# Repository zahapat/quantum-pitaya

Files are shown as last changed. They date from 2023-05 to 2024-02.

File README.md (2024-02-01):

# SQDLab FPGA Environment for Quantum Computing

Welcome to the FPGA Environment for Quantum Computing template repository.

This repository is primarily designed for use with the [Xilinx Vivado Design Suite (HLx Edition build 2020.2)](https://www.xilinx.com/support/download/index.html/content/xilinx/en/downloadNav/vivado-design-tools/archive.html) on Windows platforms.

This repository contains VLSI hardware components, PCB layouts for Red Pitaya boards, and Vivado board files for high-speed data acquisition, clock synthesis, and other purposes within a quantum laboratory.

## Prerequisites

1. [Vivado Design Suite (HLx Edition build 2020.2)](https://www.xilinx.com/support/download/index.html/content/xilinx/en/downloadNav/vivado-design-tools/archive.html)
2. [ModelSim-Intel® FPGA Standard Edition, Version 20.1std](https://www.intel.com/content/www/us/en/software-kit/750637/modelsim-intel-fpgas-standard-edition-software-version-20-1.html?)
3. [Cygwin](https://www.cygwin.com/install.html) (GNU and Open Source tools for Linux-like functionality on Windows)
4. [App Installer (Winget)](https://apps.microsoft.com/store/detail/app-installer/9NBLGGH4NNS1) available on Microsoft Store.
5. Run all scripts in the directory `'./scripts/installers/win11/'` as an administrator to configure environment variables, install chocolate, Microsoft PowerShell, PuTTY, GitHub CLI (gh), and Make.
6. If you wish to install Python as well, uncomment the fourth line in the `'RunAsAdmin2-InstallEssentialAppsWin11.bat'` file using your text editor or run the following command in your favorite terminal:

    ```shell
    choco install -yes python
    ```
7. After installing all the required software, go to the directory of this environment. Open this directory in your favourite terminal and run:
    ```shell
    make sim_init
    ```
    This will create a modelsim.ini file in the environment's root directory, necessary to launch simulations.

## Description

The tools provided with this repository serve to offer tools and VLSI source files for facilitating the development of FPGA-based projects to build optimal and resource-efficient hardware.

One can find the following subdirectories:

1. Tcl

    `./tcl` contains Tcl scripts that interact with software supporting a Tcl (Tickle) console. They are designed for automating project building and running simulations using CLI (command-line interface).

2. Scripts

    The `'./scripts'` directory consists of the following tools:

   - Python-Notebook-Based FQEnv wrapper and control tool
   - The search for optimal MMCM (Mixed Mode Clock Manager) primitives analyzer for optimal clock synthesis
   - FIR Coefficients Generator
   - Generic parameters generator
   - Data Visualizer after successful readout

3. Modules

    The `./modules` directory serves as a repository of HDL modules created throughout the development. These modules consist of hardware description and Tcl scripts for adding files to Vivado Design Suite and Modelsim in correct compile order.

4. Boards

    This directory serves as a repository of Tcl-based generators of Vivado board `'*.bd'` files necessary to integrate the project cores with various AXI-based components. It is possible to inspect such bd file in Vivado IDE.

5. PCB

    The `'./pcb'` directory contains PCB design source files and gerber files to view, review, modify, or adapt PCB designs to new designs using KiCad. Gerber files can be directly sent to a PCB manufacturer.

6. Do

    The `'./do'` directory contains do scripts that enable launching and compiling source files within ModelSim.

7. Simulator

    The `'./simulator'` directory accompanies scripts in the `./do` directory. This is the output directory of the ModelSim simualtor. Also, it contains other basic do scripts to control simulation via the ModelSim Tcl command-line. Do scripts can be programmed using Tcl.

8. Vivado

    This folder contains the Vivado project. While building the project, report files are being generated to inspect the properties of the hardware being generated, its resource utilization, timing, and more. These properties can also be inspected after launching the `FQEnv.xpr` Vivado project file located in this directory.

## Getting Started

The core unit of the FPGA Environment is the central Makefile located in the root direcotry of this repository. When opened in a text editor, it consists variables in upprecase and make targets which are named based on what one intends to do. For example, the `'make src'` target will add sources to Vivado; and `'make board'` will create and add the bd file to vivado. 

The following example reflects the main implementation flow. Run the following commands in your terminal after navigating to the root directory.

- Reset the environment:
    ```shell
    make reset
    ```

- Add all HDL sources under the given the relative Top file located in modules directory. In this case, the TOP variable defined in the Makefile will be explicitly updated by the desired source:
    ```shell
    make src TOP=top_redpitaya_125_14.sv
    ```

- Generate the Systemcerilog header file with FIR filter coefficients. All command-line arguments (e.g. INT_NUMBER_OF_TAPS, INT_COEF_WIDTH, ...) are be specified the following way:
    ```shell
    make gen_fir_coeff INT_NUMBER_OF_TAPS=13 INT_COEF_WIDTH=15 FLOAT_SAMPLING_FREQUENCY_MHZ=125.0 FLOAT_CUTOFF_FREQUENCY_MHZ=25.0
    ```

- Generate a Systemverilog header file with generic variables for the target Top file located in modules directory. The Top file is specified by updating the 'TOP' variable located in the Makefile, as shown below.
    ```shell
    make generics TOP=top_redpitaya_125_14.sv
    ```

- Run a Tcl script to generate and add the target board file, which includes the schematic system design. The target board file is specified by updating the `'BOARD'` variable declared in the Makefile, as shown below:
    ```shell
    make board BOARD=sqdlab_redpitaya_125_14_extclk
    ```

- Run all stages of implementation: synthesis, implementation, bitstream generation, hw platform generatoin (if applicable)
    ```shell
    make all
    ```

- After successful bitstream generation, the following command will copy the output bitfile together with all report available files to the `./output` directory. The output folder will be created if it does not exist.
    ```shell
    make distribute_outputs
    ```

All the abovementioned steps can be executed at once by running the following make target. This will force re-generate the desired build. You can also specify other parameters, such as GEN1_NAME declared in Makefile:
```shell
make build TOP=top_redpitaya_125_14.sv BOARD=sqdlab_redpitaya_125_14_extclk INT_NUMBER_OF_TAPS=13 INT_COEF_WIDTH=15 FLOAT_SAMPLING_FREQUENCY_MHZ=125.0 FLOAT_CUTOFF_FREQUENCY_MHZ=25.0
```

## Programming the RedPitaya board

A specific daughter Makefile is available with make commands dedicated to control the desired RedPitaya board.

To program the 10-bit RedPitaya board, run the following make command:
```shell
make rp_prog1
```

To program the 14-bit RedPitaya board:
```shell
make rp_prog2
```

To program both:
```shell
make rp_prog12
```

To run linux terminal on the 10-bit RedPitaya board:
```shell
make rp_terminal BOARD_LOCALHOST_URL=rp-f07244.local
```

To run linux terminal on the 14-bit RedPitaya board with external clock capability:
```shell
make rp_terminal BOARD_LOCALHOST_URL=rp-f0afdf.local
```

## Accessing the custom hardware of the RedPitaya board

Reading from and writing to the custom-made hardware modules is performed via AXI-Lite interface. Both `'top_redpitaya_125_10.sv'` and `'top_redpitaya_125_14.sv'` are available at the address offset 0x40600000 of the AXI-Lite address space. The `'axi4lite_fifo_readout.vhd'` as part of both of the abovementioned top modules allows for accessing two read channels and two write channels:

1. Read channel 1: address: `0x40600000` (FPGA->PC CDCC buffer FIFO channel 1)
2. Read channel 2: address: `0x40600004` (FPGA->PC CDCC buffer FIFO channel 2)
3. Write Channel 1 address: `0x40600008` (PC->FPGA CDCC buffer FIFO channel 1)
4. Write channel 2 address: `0x40600009` (PC->FPGA CDCC buffer FIFO channel 2)

Communication between the remote PC and the Red Pitaya board is performed via plink CLI commands (Putty). Read (`rp_read`) and write (`rp_write`) make targets are defined in the `'redpitaya.mk'` file.

To read 1024 values from the CDCC buffer FIFO channel 1, and save the output read_ch1.txt to the outputs directory:
```shell
make rp_read ADDRESS=0x40600000 VALUES_CNT=1024 COUT_OUTPUT_DIR=./outputs/ COUT_FILENAME=read_ch1.txt
```

To read 1024 values from the CDCC buffer FIFO channel 2, and save the output `'read_ch2.txt'` to the outputs directory:
```shell
make rp_read ADDRESS=0x40600004 VALUES_CNT=1024 COUT_OUTPUT_DIR=./outputs/ COUT_FILENAME=read_ch2.txt
```

Writing to the specific modules of the FPGA fabric uses a simple protocol. The write channel 1 uses several bits for command specification, module destination identifier, and one bit serves for concatenating the entire 32-bit wide write channel 2 packet to the write channel 1 packet.

The write channel 1 packet contains the following sections:
- *command* bits: 

    [INT_CMD_OUTPUT_WIDTH+INT_MODULE_SELECT_WIDTH : INT_MODULE_SELECT_WIDTH+1]
- module *destination* bits

    [INT_MODULE_SELECT_WIDTH : 1]
- wait for channel 2 data: 

    [0] must be true (0x1) or false (0x0)

The 32-bit wide channel 2 serves as a data channel. Data will be delivered to the destination specified by the write channel 1. The LSB must be set high to concatenate the channel write 1 with the data in the channel write 2, if needed.

If you do not wish to wait for the channel 2 and only want to send one control command throughout the write channel 1, it is possible to specify the command, module destination, and leave the LSB low. However, the required module must support this. Currently, all modules use the write channel 1 and 2 combination approach.

This example illustrates how to update the time integration value to 5. First, specify the module to be controlled:

- *cmd* = 0x0 (no need to set any of these bits high as data will be  TODO)
- *destination* = 0x3 (module  destination of the averager)
- *wait* = 0x1 (wait for channel 2 data is true)

After concatenating *cmd*, *destination*, and *wait* sections of the packet: [0x0, 0x3, 0x1] = 32'b000...0111 = 0x00000007
```shell
make rp_write ADDRESS=0x40600008 RP_CMD=0x00000007
```

Second, the following command will use the write channel 2 to update the new time integration accumulator value:
```shell
make rp_write ADDRESS=0x40600009 RP_CMD=0x00000005
```

It is possible to use up all 32 bits for it, however, the specified module may extract only a lesser number of bits depending on its input and output width specifications. More specifically, the maximum width of the `averager.sv` module to update the averaging(time integration) value is `ceil log2(INT_AVG_MAX_AVERAGE_BY)`. The `INT_AVG_MAX_AVERAGE_BY` can be updated in the main Makefile, and hardware must be re-created by running `make build` command after having this parameter updated, in case this hardware has not been created yet.

The module address map is the following. Note that module destination = 0 is invalid.
1. module destination = 1: `fifo_multichrdctrl.sv` control (both in-phase and quadrature). Select the channel and the number of reads from the `fifo_accumulator.sv` to the CDCC fifo buffer. 

Example: 
`cmd = 0 (select channel 0)` & `module destination = 1 (averager)` & `wait for channel 2 data = 1 (True)` = 0x00000003
```shell
make rp_write ADDRESS=0x40600008 RP_CMD=0x00000003
```

Use the write channel 2 to set the number of reads from the channel 0 FIFO channel. Let's read all items from the single `fifo_accumulator.sv` channel specified by INT_MULTIACC_FIFO_DEPTH in the Makefile = 1024 (0x00000400):
```shell
make rp_write ADDRESS=0x40600009 RP_CMD=0x00000400
```

2. module destination = 2: `fir_parallel.sv` control (in-phase and quadrature). Update the FIR coefficients by selecting the tap ID and its new value.

Example: 
`cmd = 0 (select tap 0)` & `module destination = 2 (FIR)` & `wait for channel 2 data = 1 (True)` = 0x00000005
```shell
make rp_write ADDRESS=0x40600008 RP_CMD=0x00000005
```

Use the write channel 2 to set the FIR coefficient 0 to a new value, e.g. 0xdeadbeef:
```shell
make rp_write ADDRESS=0x40600009 RP_CMD=0xdeadbeef
```

3. module destination = 3: `averager.sv` control (in-phase and quadrature). An example to control this module has been provided in this section above.

4. TODO: module destination = 4: `fifo_multichannel.sv`to vary the number of accumulation repetitions and multichannel FIFO dimensions instead of having it fixed by INT_MULTIACC_REPETITIONS, INT_MULTIACC_FIFO_DEPTH, and INT_MULTIACC_CHANNELS parameters.

## Usuing the FQEnv Python Notebook Makefile Build and Control Tool

*This area is currently under development and new updates are coming soon.*

This repository also contains the `fqenv.ipynb` file that serves as Python-based control tool instead of using a CLI. Also, such tool can be used as a starting point to integrating this FPGA environment into a higher-level Python ecosystem.

Methods declared in the within the `fqenv.py` allow one to perform each step of the process to build the hardware with defined parameters, program the Red Pitaya FPGA board, and control it remotely via Ethernet.

## Git: Create a New Repository

Update the `GIT_EMAIL` variable in `git.mk`. Use your email address to link Git with your Git account.
Run the following command to create a new private repo:

```shell
$ make git_new_private_repo
```

Run the following command to create a new public repository:

```shell
$ make git_new_public_repo
```

Run the following command to make the repository as a template:

```shell
$ make git_make_this_repo_template
```

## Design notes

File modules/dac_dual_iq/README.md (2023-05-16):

## Description

This module performs writing data signals to an DAC connected to the FPGA.

This core is designed for single-ended data signals.

This module has been originaly developed to interface an DAC on the Red Pitaya STEMLab 125-10 board. Therefore, further testing (for example, signal pass-through) should be performed on other devices before using this core on other platforms.

### Main Operation

1. Set generic parameters:
- INT_DAC_CHANNELS: 1 or 2
- INT_DAC_DATA_WIDTH: Enter the number of DAC data bits
- INT_AXIS_DATA_WIDTH: 32 bits typically

2. To synthesize this module in out-of-context mode, do the following:
- make reset
- make src TOP=axis_dac_ad976xastz.v
- make ooc TOP=axis_dac_ad976xastz.v

## TODO
- Add support for differential outputs

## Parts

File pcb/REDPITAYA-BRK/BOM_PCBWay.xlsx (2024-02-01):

 |  |  | xxxx xxxx xxxxx xxPCS BOM (Sample Bill of Materials)
Item # | *Designator | *Qty | Manufacturer | *Mfg Part # | Description / Value | *Package/Footprint | Type | Your Instructions / Notes
1 | ANALOG_OUT_1 | 1 | Hirose Electric Co Ltd | U.FL-R-SMT-1(10) | U.FL (UMCC) Connector Receptacle, Male Pin 50Ohm Surface Mount Solder | HRS_U.FL-R-SMT-1(10) | SMD | Datasheet: https://media.digikey.com/pdf/Data%20Sheets/Hirose%20PDFs/EDC3-302540-10.tif.pdf
2 | +5V1 | 1 | Hirose Electric Co Ltd | U.FL-R-SMT-1(10) | U.FL (UMCC) Connector Receptacle, Male Pin 50Ohm Surface Mount Solder | HRS_U.FL-R-SMT-1(10) | SMD | Datasheet: https://media.digikey.com/pdf/Data%20Sheets/Hirose%20PDFs/EDC3-302540-10.tif.pdf
3 | I2C_SDA1 | 1 | Hirose Electric Co Ltd | U.FL-R-SMT-1(10) | U.FL (UMCC) Connector Receptacle, Male Pin 50Ohm Surface Mount Solder | HRS_U.FL-R-SMT-1(10) | SMD | Datasheet: https://media.digikey.com/pdf/Data%20Sheets/Hirose%20PDFs/EDC3-302540-10.tif.pdf
4 | ANALOG_IN_3 | 1 | Hirose Electric Co Ltd | U.FL-R-SMT-1(10) | U.FL (UMCC) Connector Receptacle, Male Pin 50Ohm Surface Mount Solder | HRS_U.FL-R-SMT-1(10) | SMD | Datasheet: https://media.digikey.com/pdf/Data%20Sheets/Hirose%20PDFs/EDC3-302540-10.tif.pdf
5 | -4V1 | 1 | Hirose Electric Co Ltd | U.FL-R-SMT-1(10) | U.FL (UMCC) Connector Receptacle, Male Pin 50Ohm Surface Mount Solder | HRS_U.FL-R-SMT-1(10) | SMD | Datasheet: https://media.digikey.com/pdf/Data%20Sheets/Hirose%20PDFs/EDC3-302540-10.tif.pdf
6 | UART_RX1 | 1 | Hirose Electric Co Ltd | U.FL-R-SMT-1(10) | U.FL (UMCC) Connector Receptacle, Male Pin 50Ohm Surface Mount Solder | HRS_U.FL-R-SMT-1(10) | SMD | Datasheet: https://media.digikey.com/pdf/Data%20Sheets/Hirose%20PDFs/EDC3-302540-10.tif.pdf
7 | ANALOG_IN_0 | 1 | Hirose Electric Co Ltd | U.FL-R-SMT-1(10) | U.FL (UMCC) Connector Receptacle, Male Pin 50Ohm Surface Mount Solder | HRS_U.FL-R-SMT-1(10) | SMD | Datasheet: https://media.digikey.com/pdf/Data%20Sheets/Hirose%20PDFs/EDC3-302540-10.tif.pdf
8 | UART_TX1 | 1 | Hirose Electric Co Ltd | U.FL-R-SMT-1(10) | U.FL (UMCC) Connector Receptacle, Male Pin 50Ohm Surface Mount Solder | HRS_U.FL-R-SMT-1(10) | SMD | Datasheet: https://media.digikey.com/pdf/Data%20Sheets/Hirose%20PDFs/EDC3-302540-10.tif.pdf
9 | EXT_COM1 | 1 | Hirose Electric Co Ltd | U.FL-R-SMT-1(10) | U.FL (UMCC) Connector Receptacle, Male Pin 50Ohm Surface Mount Solder | HRS_U.FL-R-SMT-1(10) | SMD | Datasheet: https://media.digikey.com/pdf/Data%20Sheets/Hirose%20PDFs/EDC3-302540-10.tif.pdf
10 | MOSI1 | 1 | Hirose Electric Co Ltd | U.FL-R-SMT-1(10) | U.FL (UMCC) Connector Receptacle, Male Pin 50Ohm Surface Mount Solder | HRS_U.FL-R-SMT-1(10) | SMD | Datasheet: https://media.digikey.com/pdf/Data%20Sheets/Hirose%20PDFs/EDC3-302540-10.tif.pdf
11 | ANALOG_IN_1 | 1 | Hirose Electric Co Ltd | U.FL-R-SMT-1(10) | U.FL (UMCC) Connector Receptacle, Male Pin 50Ohm Surface Mount Solder | HRS_U.FL-R-SMT-1(10) | SMD | Datasheet: https://media.digikey.com/pdf/Data%20Sheets/Hirose%20PDFs/EDC3-302540-10.tif.pdf
12 | ANALOG_IN_2 | 1 | Hirose Electric Co Ltd | U.FL-R-SMT-1(10) | U.FL (UMCC) Connector Receptacle, Male Pin 50Ohm Surface Mount Solder | HRS_U.FL-R-SMT-1(10) | SMD | Datasheet: https://media.digikey.com/pdf/Data%20Sheets/Hirose%20PDFs/EDC3-302540-10.tif.pdf
13 | CLK_N1 | 1 | Hirose Electric Co Ltd | U.FL-R-SMT-1(10) | U.FL (UMCC) Connector Receptacle, Male Pin 50Ohm Surface Mount Solder | HRS_U.FL-R-SMT-1(10) | SMD | Datasheet: https://media.digikey.com/pdf/Data%20Sheets/Hirose%20PDFs/EDC3-302540-10.tif.pdf
14 | ANALOG_OUT_2 | 1 | Hirose Electric Co Ltd | U.FL-R-SMT-1(10) | U.FL (UMCC) Connector Receptacle, Male Pin 50Ohm Surface Mount Solder | HRS_U.FL-R-SMT-1(10) | SMD | Datasheet: https://media.digikey.com/pdf/Data%20Sheets/Hirose%20PDFs/EDC3-302540-10.tif.pdf
15 | ANALOG_OUT_0 | 1 | Hirose Electric Co Ltd | U.FL-R-SMT-1(10) | U.FL (UMCC) Connector Receptacle, Male Pin 50Ohm Surface Mount Solder | HRS_U.FL-R-SMT-1(10) | SMD | Datasheet: https://media.digikey.com/pdf/Data%20Sheets/Hirose%20PDFs/EDC3-302540-10.tif.pdf
16 | MISO1 | 1 | Hirose Electric Co Ltd | U.FL-R-SMT-1(10) | U.FL (UMCC) Connector Receptacle, Male Pin 50Ohm Surface Mount Solder | HRS_U.FL-R-SMT-1(10) | SMD | Datasheet: https://media.digikey.com/pdf/Data%20Sheets/Hirose%20PDFs/EDC3-302540-10.tif.pdf
17 | ANALOG_OUT_3 | 1 | Hirose Electric Co Ltd | U.FL-R-SMT-1(10) | U.FL (UMCC) Connector Receptacle, Male Pin 50Ohm Surface Mount Solder | HRS_U.FL-R-SMT-1(10) | SMD | Datasheet: https://media.digikey.com/pdf/Data%20Sheets/Hirose%20PDFs/EDC3-302540-10.tif.pdf
18 | CLK_P1 | 1 | Hirose Electric Co Ltd | U.FL-R-SMT-1(10) | U.FL (UMCC) Connector Receptacle, Male Pin 50Ohm Surface Mount Solder | HRS_U.FL-R-SMT-1(10) | SMD | Datasheet: https://media.digikey.com/pdf/Data%20Sheets/Hirose%20PDFs/EDC3-302540-10.tif.pdf
19 | SCLK1 | 1 | Hirose Electric Co Ltd | U.FL-R-SMT-1(10) | U.FL (UMCC) Connector Receptacle, Male Pin 50Ohm Surface Mount Solder | HRS_U.FL-R-SMT-1(10) | SMD | Datasheet: https://media.digikey.com/pdf/Data%20Sheets/Hirose%20PDFs/EDC3-302540-10.tif.pdf
20 | I2C_SCL1 | 1 | Hirose Electric Co Ltd | U.FL-R-SMT-1(10) | U.FL (UMCC) Connector Receptacle, Male Pin 50Ohm Surface Mount Solder | HRS_U.FL-R-SMT-1(10) | SMD | Datasheet: https://media.digikey.com/pdf/Data%20Sheets/Hirose%20PDFs/EDC3-302540-10.tif.pdf
21 | CS1 | 1 | Hirose Electric Co Ltd | U.FL-R-SMT-1(10) | U.FL (UMCC) Connector Receptacle, Male Pin 50Ohm Surface Mount Solder | HRS_U.FL-R-SMT-1(10) | SMD | Datasheet: https://media.digikey.com/pdf/Data%20Sheets/Hirose%20PDFs/EDC3-302540-10.tif.pdf
22 | J1 | 1 | TE Connectivity AMP Connectors | 6-534206-3 | 26 Position Receptacle Connector 0.100" (2.54mm) Through Hole Gold | TE_6-534206-3 | SMD | Datasheet: https://www.te.com/commerce/DocumentDelivery/DDEController?Action=srchrtrv&DocNm=534206&DocType=Customer+Drawing&DocLang=English

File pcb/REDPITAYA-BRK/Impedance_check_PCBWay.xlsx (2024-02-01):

 |  |  | Impedance Check
Item # | *Trace Name | *Impedance Style | *Trace width/spacing | *Controled trace location, layer | *Impedance Value and Tolerance | *Reference layer | Your Instructions / Notes
1 | CLK_N, CLK_P | Coupled Coplanar Waveguide with Backside | Trace Width = 0.1524 mm, Copper Pour Clearance = 0.35 mm, Differential Pair Gap = 0.197 mm | F.Cu | Zdiff = 100 Ω +/- 8 Ω | In1.Cu
2 | ai0 | Coplanar Waveguide with Backside | Width = 0.2 mm, Copper Pour Clearance = 0.1524 mm | F.Cu | Z = 50 Ω +/- 4 Ω | In1.Cu
3 | ai1 | Coplanar Waveguide with Backside | Width = 0.2 mm, Copper Pour Clearance = 0.1524 mm | F.Cu | Z = 50 Ω +/- 4 Ω | In1.Cu
4 | ai2 | Coplanar Waveguide with Backside | Width = 0.2 mm, Copper Pour Clearance = 0.1524 mm | F.Cu | Z = 50 Ω +/- 4 Ω | In1.Cu
5 | ai3 | Coplanar Waveguide with Backside | Width = 0.2 mm, Copper Pour Clearance = 0.1524 mm | F.Cu | Z = 50 Ω +/- 4 Ω | In1.Cu
6 | ao0 | Coplanar Waveguide with Backside | Width = 0.2 mm, Copper Pour Clearance = 0.1524 mm | F.Cu | Z = 50 Ω +/- 4 Ω | In1.Cu
7 | ao1 | Coplanar Waveguide with Backside | Width = 0.2 mm, Copper Pour Clearance = 0.1524 mm | F.Cu | Z = 50 Ω +/- 4 Ω | In1.Cu
8 | ao2 | Coplanar Waveguide with Backside | Width = 0.2 mm, Copper Pour Clearance = 0.1524 mm | F.Cu | Z = 50 Ω +/- 4 Ω | In1.Cu
9 | ao3 | Coplanar Waveguide with Backside | Width = 0.2 mm, Copper Pour Clearance = 0.1524 mm | F.Cu | Z = 50 Ω +/- 4 Ω | In1.Cu

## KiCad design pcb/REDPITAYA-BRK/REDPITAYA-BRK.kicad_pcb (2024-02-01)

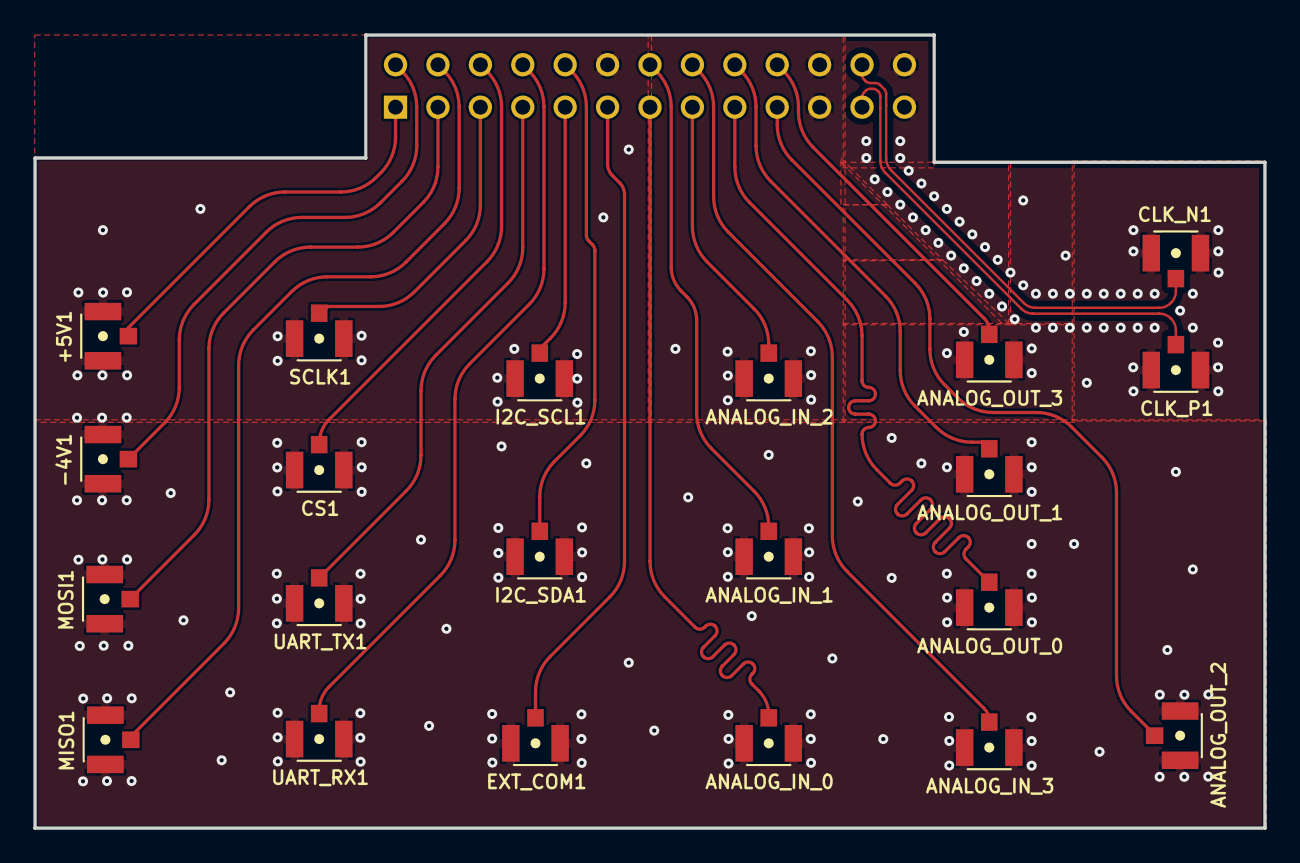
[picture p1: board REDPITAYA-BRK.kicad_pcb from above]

Board: 4 copper layers, 73.7 x 47.5 mm, 22 parts (1 on the bottom side), 22 nets.

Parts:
+5V1: U.FL-R-SMT-1(10); HRS_U.FL-R-SMT-1(10)
-4V1: U.FL-R-SMT-1(10); HRS_U.FL-R-SMT-1(10)
ANALOG_IN_0, ANALOG_IN_1, ANALOG_IN_2, ANALOG_IN_3: U.FL-R-SMT-1(10); HRS_U.FL-R-SMT-1(10)
ANALOG_OUT_0, ANALOG_OUT_1, ANALOG_OUT_2, ANALOG_OUT_3: U.FL-R-SMT-1(10); HRS_U.FL-R-SMT-1(10)
CLK_N1: U.FL-R-SMT-1(10); HRS_U.FL-R-SMT-1(10)
CLK_P1: U.FL-R-SMT-1(10); HRS_U.FL-R-SMT-1(10)
CS1: U.FL-R-SMT-1(10); HRS_U.FL-R-SMT-1(10)
EXT_COM1: U.FL-R-SMT-1(10); HRS_U.FL-R-SMT-1(10)
I2C_SCL1, I2C_SDA1: U.FL-R-SMT-1(10); HRS_U.FL-R-SMT-1(10)
J1: 6-534206-3; TE_6-534206-3
MISO1: U.FL-R-SMT-1(10); HRS_U.FL-R-SMT-1(10)
MOSI1: U.FL-R-SMT-1(10); HRS_U.FL-R-SMT-1(10)
SCLK1: U.FL-R-SMT-1(10); HRS_U.FL-R-SMT-1(10)
UART_RX1: U.FL-R-SMT-1(10); HRS_U.FL-R-SMT-1(10)
UART_TX1: U.FL-R-SMT-1(10); HRS_U.FL-R-SMT-1(10)

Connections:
/CLK_N: CLK_N1.2 (SIG), J1.25
/CLK_P: CLK_P1.2 (SIG), J1.12
/ai0: ANALOG_IN_0.2 (SIG), J1.7
/ai1: ANALOG_IN_1.2 (SIG), J1.20
/ai2: ANALOG_IN_2.2 (SIG), J1.8
/ai3: ANALOG_IN_3.2 (SIG), J1.21
/ao0: ANALOG_OUT_0.2 (SIG), J1.9
/ao1: ANALOG_OUT_1.2 (SIG), J1.22
/ao2: ANALOG_OUT_2.2 (SIG), J1.10
/ao3: ANALOG_OUT_3.2 (SIG), J1.23
/cs: CS1.2 (SIG), J1.16
/ext_com: EXT_COM1.2 (SIG), J1.6
/i2c_scl: I2C_SCL1.2 (SIG), J1.5
/i2c_sda: I2C_SDA1.2 (SIG), J1.18
/m4v: -4V1.2 (SIG), J1.14
/miso: J1.15, MISO1.2 (SIG)
/mosi: J1.2, MOSI1.2 (SIG)
/p5v: +5V1.2 (SIG), J1.1
/sclk: J1.3, SCLK1.2 (SIG)
/uart_rx: J1.17, UART_RX1.2 (SIG)
/uart_tx: J1.4, UART_TX1.2 (SIG)
GND: +5V1.1 (GND), +5V1.3 (GND), -4V1.1 (GND), -4V1.3 (GND), ANALOG_IN_0.1 (GND), ANALOG_IN_0.3 (GND), ANALOG_IN_1.1 (GND), ANALOG_IN_1.3 (GND), ANALOG_IN_2.1 (GND), ANALOG_IN_2.3 (GND), ANALOG_IN_3.1 (GND), ANALOG_IN_3.3 (GND), ANALOG_OUT_0.1 (GND), ANALOG_OUT_0.3 (GND), ANALOG_OUT_1.1 (GND), ANALOG_OUT_1.3 (GND), ANALOG_OUT_2.1 (GND), ANALOG_OUT_2.3 (GND), ANALOG_OUT_3.1 (GND), ANALOG_OUT_3.3 (GND), CLK_N1.1 (GND), CLK_N1.3 (GND), CLK_P1.1 (GND), CLK_P1.3 (GND), CS1.1 (GND), CS1.3 (GND), EXT_COM1.1 (GND), EXT_COM1.3 (GND), I2C_SCL1.1 (GND), I2C_SCL1.3 (GND), I2C_SDA1.1 (GND), I2C_SDA1.3 (GND), J1.11, J1.13, J1.19, J1.24, J1.26, MISO1.1 (GND), MISO1.3 (GND), MOSI1.1 (GND), MOSI1.3 (GND), SCLK1.1 (GND), SCLK1.3 (GND), UART_RX1.1 (GND), UART_RX1.3 (GND), UART_TX1.1 (GND), UART_TX1.3 (GND)

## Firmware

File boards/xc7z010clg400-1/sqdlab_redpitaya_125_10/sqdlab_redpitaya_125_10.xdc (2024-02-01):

set_property CFGBVS VCCO [current_design]
# set_property CONFIG_VOLTAGE 3.3 [current_design]
set_property CONFIG_VOLTAGE 2.5 [current_design]


############################################################################
## ADC System Clock
############################################################################

# Clock Input from ADC
set_property IOSTANDARD LVCMOS18 [get_ports in_adc_clk_p_0]
set_property PACKAGE_PIN U18 [get_ports in_adc_clk_p_0]

create_clock -name in_adc_clk_p_0 -period 8.000 [get_ports in_adc_clk_p_0]


############################################################################
## ADC
############################################################################

# Data: Channel 1
set_property IOSTANDARD LVCMOS18 [get_ports {in_data_ch1_0[*]}]
set_property IOB TRUE [get_ports {in_data_ch1_0[*]}]

set_property PACKAGE_PIN W14 [get_ports {in_data_ch1_0[0]}]
set_property PACKAGE_PIN Y14 [get_ports {in_data_ch1_0[1]}]
set_property PACKAGE_PIN W13 [get_ports {in_data_ch1_0[2]}]
set_property PACKAGE_PIN V12 [get_ports {in_data_ch1_0[3]}]
set_property PACKAGE_PIN V13 [get_ports {in_data_ch1_0[4]}]
set_property PACKAGE_PIN T14 [get_ports {in_data_ch1_0[5]}]
set_property PACKAGE_PIN T15 [get_ports {in_data_ch1_0[6]}]
set_property PACKAGE_PIN V15 [get_ports {in_data_ch1_0[7]}]
set_property PACKAGE_PIN T16 [get_ports {in_data_ch1_0[8]}]
set_property PACKAGE_PIN V16 [get_ports {in_data_ch1_0[9]}]

# Data: Channel 2
set_property IOSTANDARD LVCMOS18 [get_ports {in_data_ch2_0[*]}]
set_property IOB TRUE [get_ports {in_data_ch2_0[*]}]

set_property PACKAGE_PIN R19 [get_ports {in_data_ch2_0[0]}]
set_property PACKAGE_PIN T20 [get_ports {in_data_ch2_0[1]}]
set_property PACKAGE_PIN T19 [get_ports {in_data_ch2_0[2]}]
set_property PACKAGE_PIN U20 [get_ports {in_data_ch2_0[3]}]
set_property PACKAGE_PIN V20 [get_ports {in_data_ch2_0[4]}]
set_property PACKAGE_PIN W20 [get_ports {in_data_ch2_0[5]}]
set_property PACKAGE_PIN W19 [get_ports {in_data_ch2_0[6]}]
set_property PACKAGE_PIN Y19 [get_ports {in_data_ch2_0[7]}]
set_property PACKAGE_PIN W18 [get_ports {in_data_ch2_0[8]}]
set_property PACKAGE_PIN Y18 [get_ports {in_data_ch2_0[9]}]

# Duty Cycle Clock Stabilizer
set_property IOSTANDARD LVCMOS18 [get_ports adc_i_clkstb_0]
set_property PACKAGE_PIN V18 [get_ports adc_i_clkstb_0]
set_property SLEW FAST [get_ports adc_i_clkstb_0]
set_property DRIVE 8 [get_ports adc_i_clkstb_0]


############################################################################
## DAC
############################################################################

# DAC Data Signals
# set_property IOSTANDARD LVCMOS33 [get_ports {dac_o_data_0[*]}]
set_property IOSTANDARD LVCMOS25 [get_ports {dac_o_data_0[*]}]
set_property SLEW SLOW [get_ports {dac_o_data_0[*]}]
set_property DRIVE 4 [get_ports {dac_o_data_0[*]}]
# set_property IOB TRUE [get_ports {dac_o_data_0[*]}]


set_property PACKAGE_PIN K19 [get_ports {dac_o_data_0[0]}]
set_property PACKAGE_PIN J19 [get_ports {dac_o_data_0[1]}]
set_property PACKAGE_PIN J20 [get_ports {dac_o_data_0[2]}]
set_property PACKAGE_PIN H20 [get_ports {dac_o_data_0[3]}]
set_property PACKAGE_PIN G19 [get_ports {dac_o_data_0[4]}]
set_property PACKAGE_PIN G20 [get_ports {dac_o_data_0[5]}]
set_property PACKAGE_PIN F19 [get_ports {dac_o_data_0[6]}]
set_property PACKAGE_PIN F20 [get_ports {dac_o_data_0[7]}]
set_property PACKAGE_PIN D20 [get_ports {dac_o_data_0[8]}]
set_property PACKAGE_PIN D19 [get_ports {dac_o_data_0[9]}]

# DAC IQ Control Signals
# set_property IOSTANDARD LVCMOS33 [get_ports dac_o_iqwrt_0]
set_property IOSTANDARD LVCMOS25 [get_ports dac_o_iqwrt_0]
set_property SLEW FAST [get_ports dac_o_iqwrt_0]
set_property DRIVE 8 [get_ports dac_o_iqwrt_0]
set_property IOB TRUE [get_ports {dac_o_iqwrt_0}]
set_property PACKAGE_PIN M17 [get_ports dac_o_iqwrt_0]

# set_property IOSTANDARD LVCMOS33 [get_ports dac_o_iqsel_0]
set_property IOSTANDARD LVCMOS25 [get_ports dac_o_iqsel_0]
set_property SLEW FAST [get_ports dac_o_iqsel_0]
set_property DRIVE 8 [get_ports dac_o_iqsel_0]
set_property IOB TRUE [get_ports {dac_o_iqsel_0}]
set_property PACKAGE_PIN N16 [get_ports dac_o_iqsel_0]

# set_property IOSTANDARD LVCMOS33 [get_ports dac_o_iqclk_0]
set_property IOSTANDARD LVCMOS25 [get_ports dac_o_iqclk_0]
set_property SLEW FAST [get_ports dac_o_iqclk_0]
set_property DRIVE 8 [get_ports dac_o_iqclk_0]
set_property IOB TRUE [get_ports {dac_o_iqclk_0}]
set_property PACKAGE_PIN M18 [get_ports dac_o_iqclk_0]

# set_property IOSTANDARD LVCMOS33 [get_ports dac_o_iqrst_0]
set_property IOSTANDARD LVCMOS25 [get_ports dac_o_iqrst_0]
set_property SLEW FAST [get_ports dac_o_iqrst_0]
set_property DRIVE 8 [get_ports dac_o_iqrst_0]
set_property IOB TRUE [get_ports {dac_o_iqrst_0}]
set_property PACKAGE_PIN N15 [get_ports dac_o_iqrst_0]


############################################################################
## LEDS
############################################################################

# set_property IOSTANDARD LVCMOS33 [get_ports {leds_0[*]}]
set_property IOSTANDARD LVCMOS25 [get_ports {leds_0[*]}]
set_property SLEW SLOW [get_ports {leds_0[*]}]
set_property DRIVE 8 [get_ports {leds_0[*]}]

set_property PACKAGE_PIN F16 [get_ports {leds_0[0]}]
set_property PACKAGE_PIN F17 [get_ports {leds_0[1]}]
set_property PACKAGE_PIN G15 [get_ports {leds_0[2]}]
set_property PACKAGE_PIN H15 [get_ports {leds_0[3]}]
set_property PACKAGE_PIN K14 [get_ports {leds_0[4]}]
set_property PACKAGE_PIN G14 [get_ports {leds_0[5]}]
set_property PACKAGE_PIN J15 [get_ports {leds_0[6]}]
set_property PACKAGE_PIN J14 [get_ports {leds_0[7]}]



############################################################################
## EXPANSION CONNECTOR 1
############################################################################

# NOTE:
# [Place 30-574] Poor placement for routing between an IO pin and BUFG. If this sub optimal condition is acceptable for this design, you may use the CLOCK_DEDICATED_ROUTE constraint in the .xdc file to demote this message to a WARNING. However, the use of this override is highly discouraged. These examples can be used directly in the .xdc file to override this clock rule.
# < set_property CLOCK_DEDICATED_ROUTE FALSE [get_nets i_ext_clk_0_IBUF] >

# i_ext_clk_0_IBUF_inst (IBUF.O) is locked to IOB_X0Y51
#  and sqdlab_redpitaya_125_10_i/top_redpitaya_125_10_0/inst/inst_top_redpitaya_125_10/inst_adc_clk_bufg2 (BUFG.I) 
#  is provisionally placed by clockplacer on BUFGCTRL_X0Y19

# Reasons for the following step:
# The 10 MHz clock input is lower than the allowed frequency range of a PLL (19 MHz)
# MMCM does support 10 MHz input signal, however, due to the location mismatch
# of the MMCM and the CC pin, placer cannot find a solution for routing the
# CC pin to the clock tree without significant time delays. This may result in
# timing violations.
# However, the output of the MMCM goes straight to the output of the device,
# thus no logic will be driven by this signal. Hence, the following command can
# be used to allow routing the CC and MMCM not only via via CLOCK_DEDICATED_ROUTE, 
# but also via routes in the programmable fabric:
set_property CLOCK_DEDICATED_ROUTE FALSE [get_nets i_ext_clk_0_IBUF]


# DIO1_N (on PCB brk board: sclk)
set_property IOSTANDARD LVCMOS25 [get_ports {i_ext_clk_0}]
set_property IOB TRUE [get_ports {i_ext_clk_0}]
set_property SLEW FAST [get_ports {i_ext_clk_0}]
# set_property DRIVE 8 [get_ports {i_ext_clk_0}]
set_property PACKAGE_PIN H16 [get_ports {i_ext_clk_0}]

create_clock -name i_ext_clk_0 -period 100.000 [get_ports i_ext_clk_0]

# DIO0_P (on PCB brk board: mosi)
# set_property IOSTANDARD LVDS_25 [get_ports {o_clk_lvds_p_0}]
set_property IOSTANDARD LVCMOS25 [get_ports {o_clk_lvds_p_0}]
# set_property IOB TRUE [get_ports {o_clk_lvds_p_0}]
# set_property SLEW FAST [get_ports {o_clk_lvds_p_0}]
# set_property DRIVE 8 [get_ports {o_clk_lvds_p_0}]
set_property PACKAGE_PIN G17 [get_ports {o_clk_lvds_p_0}]

# DIO0_N (on PCB brk board: miso)
# set_property IOSTANDARD LVDS_25 [get_ports {o_clk_lvds_n_0}]
set_property IOSTANDARD LVCMOS25 [get_ports {o_clk_lvds_n_0}]
# set_property IOB TRUE [get_ports {o_clk_lvds_n_0}]
# set_property SLEW FAST [get_ports {o_clk_lvds_n_0}]
# set_property DRIVE 8 [get_ports {o_clk_lvds_n_0}]
set_property PACKAGE_PIN G18 [get_ports {o_clk_lvds_n_0}]


# DIO1_N (on PCB brk board: analog_input_3)
set_property IOSTANDARD LVCMOS25 [get_ports {i_acc_trigger_1_0}]
set_property IOB TRUE [get_ports {i_acc_trigger_1_0}]
set_property SLEW FAST [get_ports {i_acc_trigger_1_0}]
# set_property DRIVE 8 [get_ports {i_ext_clk_0}]
set_property PACKAGE_PIN J16 [get_ports {i_acc_trigger_1_0}]



############################################################################
## EXPANSION CONNECTOR 2
############################################################################

# Analog Input Ports *NOT USED*
# set_property IOSTANDARD LVCMOS33 [get_ports {analog_in_p_0[*]}]
# set_property IOSTANDARD LVCMOS33 [get_ports {analog_in_n_0[*]}]
# set_property SLEW FAST [get_ports {analog_in_p_0[*]}]
# set_property SLEW FAST [get_ports {analog_in_n_0[*]}]
# set_property DRIVE 8 [get_ports {analog_in_p_0[*]}]
# set_property DRIVE 8 [get_ports {analog_in_n_0[*]}]

# set_property PACKAGE_PIN B19 [get_ports {analog_in_p_0[0]}] # AIFP0
# set_property PACKAGE_PIN A20 [get_ports {analog_in_n_0[0]}] # AIFN0
# set_property PACKAGE_PIN C20 [get_ports {analog_in_p_0[1]}] # AIFP1
# set_property PACKAGE_PIN B20 [get_ports {analog_in_n_0[1]}] # AIFN1
# set_property PACKAGE_PIN E17 [get_ports {analog_in_p_0[2]}] # AIFP2
# set_property PACKAGE_PIN D18 [get_ports {analog_in_n_0[2]}] # AIFN2
# set_property PACKAGE_PIN E18 [get_ports {analog_in_p_0[3]}] # AIFP3
# set_property PACKAGE_PIN E19 [get_ports {analog_in_n_0[3]}] # AIFN3

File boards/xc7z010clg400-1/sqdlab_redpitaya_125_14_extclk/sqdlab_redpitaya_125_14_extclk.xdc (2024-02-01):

# set_property CFGBVS VCCO [current_design]
# set_property CONFIG_VOLTAGE 3.3 [current_design]


############################################################################
## ADC System Clock
############################################################################

# Clock Input from ADC
set_property IOSTANDARD DIFF_HSTL_I_18 [get_ports in_adc_clk_p_0]
set_property IOSTANDARD DIFF_HSTL_I_18 [get_ports in_adc_clk_n_0]
set_property PACKAGE_PIN U18 [get_ports in_adc_clk_p_0]
set_property PACKAGE_PIN U19 [get_ports in_adc_clk_n_0]

# Clock Output
# set_property IOSTANDARD LVCMOS18 [get_ports adc_enc_p_o]
# set_property IOSTANDARD LVCMOS18 [get_ports adc_enc_n_o]
# set_property SLEW FAST [get_ports adc_enc_p_o]
# set_property SLEW FAST [get_ports adc_enc_n_o]
# set_property DRIVE 8 [get_ports adc_enc_p_o]
# set_property DRIVE 8 [get_ports adc_enc_n_o]
# set_property PACKAGE_PIN N20 [get_ports adc_enc_p_o]
# set_property PACKAGE_PIN P20 [get_ports adc_enc_n_o]


############################################################################
## ADC
############################################################################

# ADC Data Signals
set_property IOSTANDARD LVCMOS18 [get_ports {in_data_ch*_0[*]}]
set_property IOB TRUE [get_ports {in_data_ch*_0[*]}]

set_property PACKAGE_PIN Y17 [get_ports {in_data_ch1_0[0]}]
set_property PACKAGE_PIN W16 [get_ports {in_data_ch1_0[1]}]
set_property PACKAGE_PIN Y16 [get_ports {in_data_ch1_0[2]}]
set_property PACKAGE_PIN W15 [get_ports {in_data_ch1_0[3]}]
set_property PACKAGE_PIN W14 [get_ports {in_data_ch1_0[4]}]
set_property PACKAGE_PIN Y14 [get_ports {in_data_ch1_0[5]}]
set_property PACKAGE_PIN W13 [get_ports {in_data_ch1_0[6]}]
set_property PACKAGE_PIN V12 [get_ports {in_data_ch1_0[7]}]
set_property PACKAGE_PIN V13 [get_ports {in_data_ch1_0[8]}]
set_property PACKAGE_PIN T14 [get_ports {in_data_ch1_0[9]}]
set_property PACKAGE_PIN T15 [get_ports {in_data_ch1_0[10]}]
set_property PACKAGE_PIN V15 [get_ports {in_data_ch1_0[11]}]
set_property PACKAGE_PIN T16 [get_ports {in_data_ch1_0[12]}]
set_property PACKAGE_PIN V16 [get_ports {in_data_ch1_0[13]}]

set_property PACKAGE_PIN R18 [get_ports {in_data_ch2_0[0]}]
set_property PACKAGE_PIN P16 [get_ports {in_data_ch2_0[1]}]
set_property PACKAGE_PIN P18 [get_ports {in_data_ch2_0[2]}]
set_property PACKAGE_PIN N17 [get_ports {in_data_ch2_0[3]}]
set_property PACKAGE_PIN R19 [get_ports {in_data_ch2_0[4]}]
set_property PACKAGE_PIN T20 [get_ports {in_data_ch2_0[5]}]
set_property PACKAGE_PIN T19 [get_ports {in_data_ch2_0[6]}]
set_property PACKAGE_PIN U20 [get_ports {in_data_ch2_0[7]}]
set_property PACKAGE_PIN V20 [get_ports {in_data_ch2_0[8]}]
set_property PACKAGE_PIN W20 [get_ports {in_data_ch2_0[9]}]
set_property PACKAGE_PIN W19 [get_ports {in_data_ch2_0[10]}]
set_property PACKAGE_PIN Y19 [get_ports {in_data_ch2_0[11]}]
set_property PACKAGE_PIN W18 [get_ports {in_data_ch2_0[12]}]
set_property PACKAGE_PIN Y18 [get_ports {in_data_ch2_0[13]}]

# ADC Clock Duty Cycle Stabilizer (CSn)
set_property IOSTANDARD LVCMOS18 [get_ports adc_i_clkstb_0]
set_property PACKAGE_PIN V18 [get_ports adc_i_clkstb_0]
set_property SLEW FAST [get_ports adc_i_clkstb_0]
set_property DRIVE 8 [get_ports adc_i_clkstb_0]


############################################################################
## DAC
############################################################################

# DAC Data Signals
# set_property IOB TRUE [get_ports {dac_dat_o[*]}]
set_property IOSTANDARD LVCMOS33 [get_ports {dac_o_data_0[*]}]
set_property SLEW SLOW [get_ports {dac_o_data_0[*]}]
set_property DRIVE 4 [get_ports {dac_o_data_0[*]}]

set_property PACKAGE_PIN M19 [get_ports {dac_o_data_0[0]}]
set_property PACKAGE_PIN M20 [get_ports {dac_o_data_0[1]}]
set_property PACKAGE_PIN L19 [get_ports {dac_o_data_0[2]}]
set_property PACKAGE_PIN L20 [get_ports {dac_o_data_0[3]}]
set_property PACKAGE_PIN K19 [get_ports {dac_o_data_0[4]}]
set_property PACKAGE_PIN J19 [get_ports {dac_o_data_0[5]}]
set_property PACKAGE_PIN J20 [get_ports {dac_o_data_0[6]}]
set_property PACKAGE_PIN H20 [get_ports {dac_o_data_0[7]}]
set_property PACKAGE_PIN G19 [get_ports {dac_o_data_0[8]}]
set_property PACKAGE_PIN G20 [get_ports {dac_o_data_0[9]}]
set_property PACKAGE_PIN F19 [get_ports {dac_o_data_0[10]}]
set_property PACKAGE_PIN F20 [get_ports {dac_o_data_0[11]}]
set_property PACKAGE_PIN D20 [get_ports {dac_o_data_0[12]}]
set_property PACKAGE_PIN D19 [get_ports {dac_o_data_0[13]}]

# DAC IQ Control Signals
# set_property IOB TRUE [get_ports {dac_o_iq*_o}]
set_property IOSTANDARD LVCMOS33 [get_ports dac_o_iq*_0]
set_property SLEW FAST [get_ports dac_o_iq*_0]
set_property DRIVE 8 [get_ports dac_o_iq*_0]

set_property PACKAGE_PIN M17 [get_ports dac_o_iqwrt_0]
set_property PACKAGE_PIN N16 [get_ports dac_o_iqsel_0]
set_property PACKAGE_PIN M18 [get_ports dac_o_iqclk_0]
set_property PACKAGE_PIN N15 [get_ports dac_o_iqrst_0]


############################################################################
## PWM
############################################################################
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

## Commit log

2023-05-16 feat: Perform read from fifo on Red Pitaya board
2024-02-01 refactor: Refresh codebase
    [BOM_PCBWay.xlsx, FMC-HPC-BRK-B_Adhesive.gbr, FMC-HPC-BRK-B_Courtyard.gbr, FMC-HPC-BRK-B_Cu.gbr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]
